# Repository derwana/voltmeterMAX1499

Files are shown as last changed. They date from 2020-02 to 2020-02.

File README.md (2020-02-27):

# voltmeterMAX1499
The voltmeterMAX1499 is - as you may expect by the name - a voltmeter based on the MAX1499 chip by maximinterated.

Started as a university project (v1) to be put into the student laboratories consoles as a highly accurat voltmeter (guess what: it never happend), it later got reworked (v2) to be used with a refrence voltage and two different seven-segment-display-boards.

## 1 precepts
1. boards for the IC and the 'display' have to be seperate
2. board dimensions not given, but as small as possible
3. six seven-segments – one for the '-' and five for the digits
4. multiple options for displaying (0kR for selection)
	1. decimals by chip
	2. decimals by user
5. boards to be connected by male and female headers
6. drills for spacers and mounting
7. use smd parts

## 2 prototype pictures
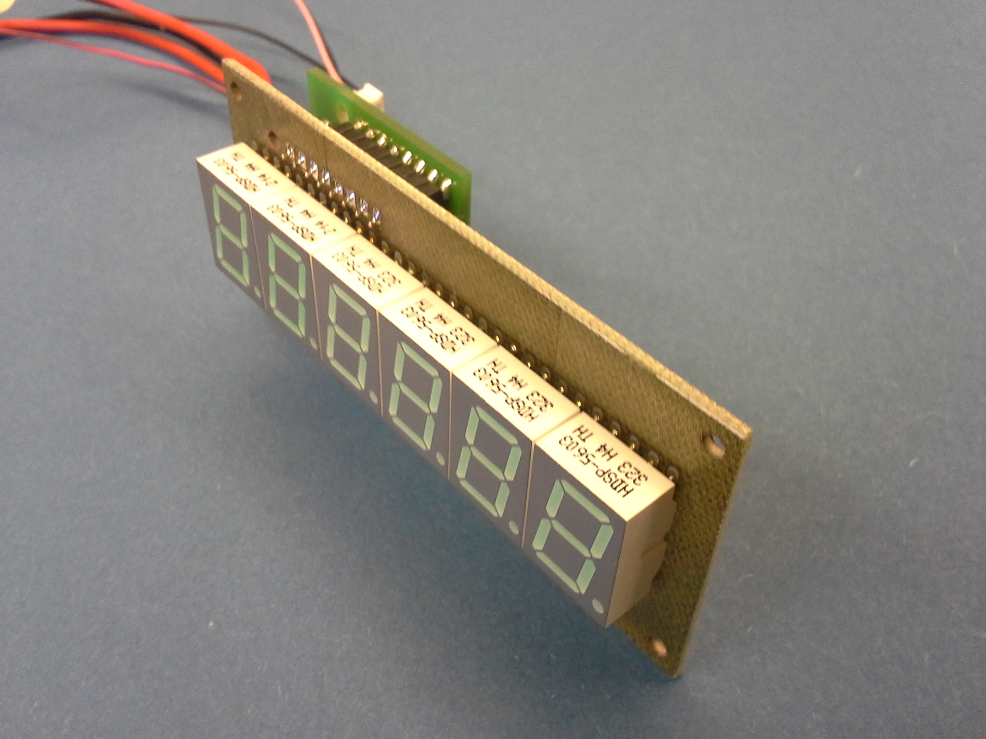
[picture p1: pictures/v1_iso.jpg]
prototype v1

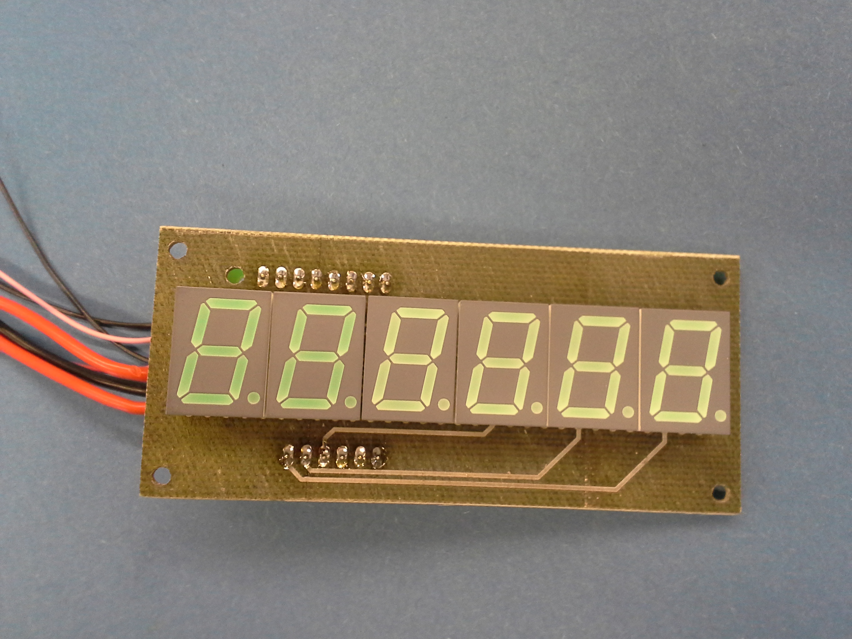
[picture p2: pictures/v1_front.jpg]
prototype v1 front

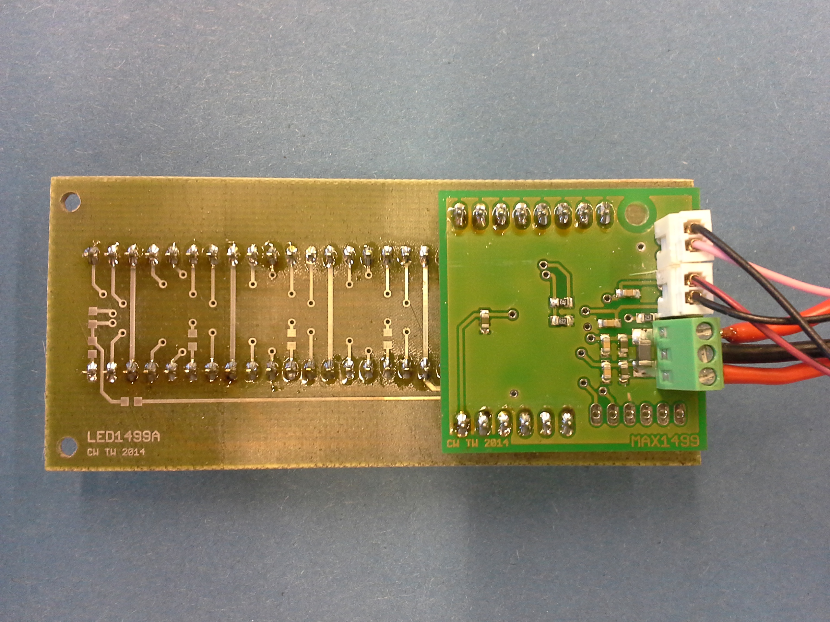
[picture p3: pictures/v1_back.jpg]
prototype v1 back


## 3 prototype testing
on X3: 5V DC (Vcc)
on X1: 1.000V DC (testvoltage by signalgenerator)

Measuring the current consumption is a good tool to determin a correctly working board.

One seven-segment-element consumes 20mA on max brightness and all tiles lit. Six of them are used, so a current consumption of ca. 120mA is expected.

With R3=24kR and displaying 18882, the current flowing is 117mA.
On idle, current consumption as expected of the datasheet.

## 4 Costs
estimated 45,00 € (per unit)
* PCBs 16.65€
* MAX1499 13.10€
* 7-Segments 1.00€-2.00€ (per segment-unit)

## 5 pictures of v2
Connections:
* potentiometer for dimming (black/pink)
* Vcc (black/red)
* voltage to measure (black/orange)
* programming interface (brown/red/orange/yellow)

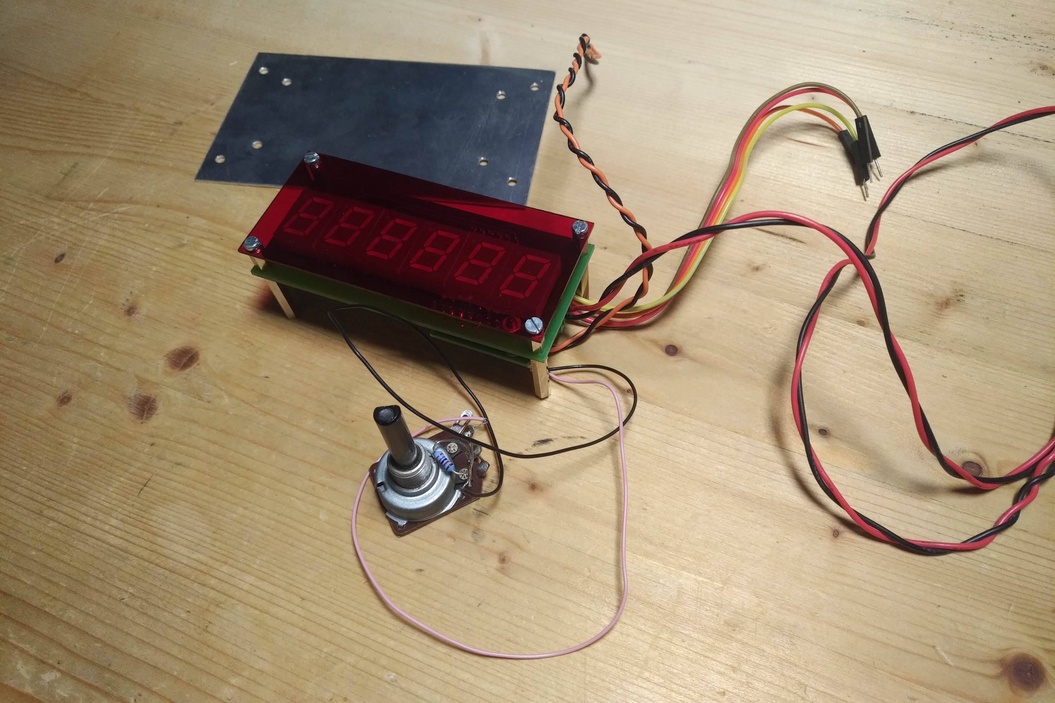
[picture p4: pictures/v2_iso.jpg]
prototype v2

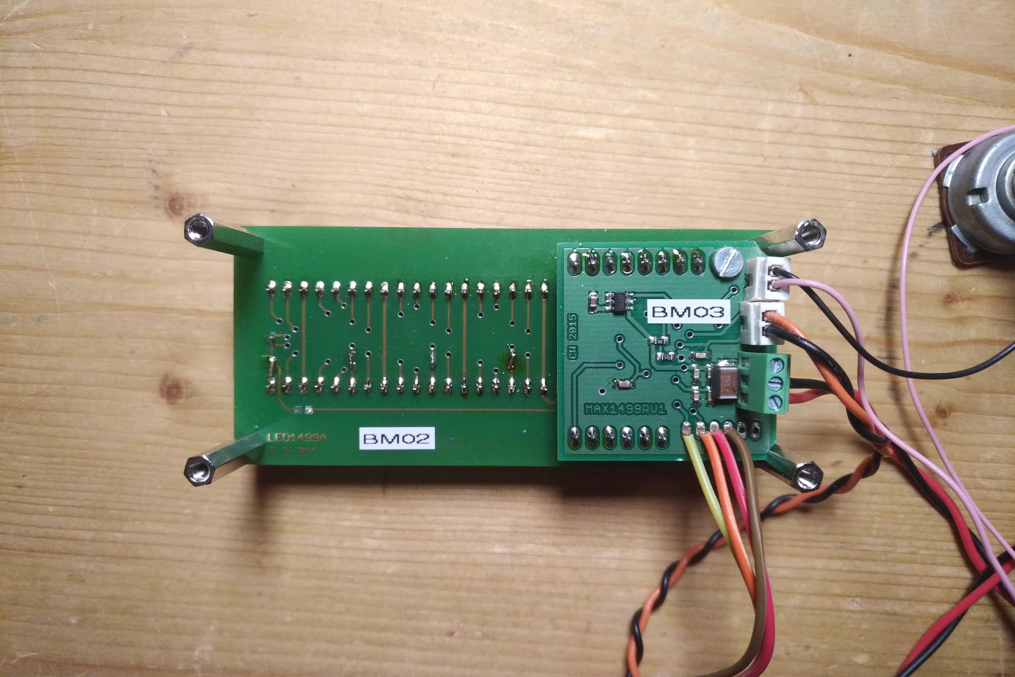
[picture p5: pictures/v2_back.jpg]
prototype v2 back


## 6 further possible improvements (by programming)
* moving decimal point
* using internal reference of MAX1499
* reading measurements over serial

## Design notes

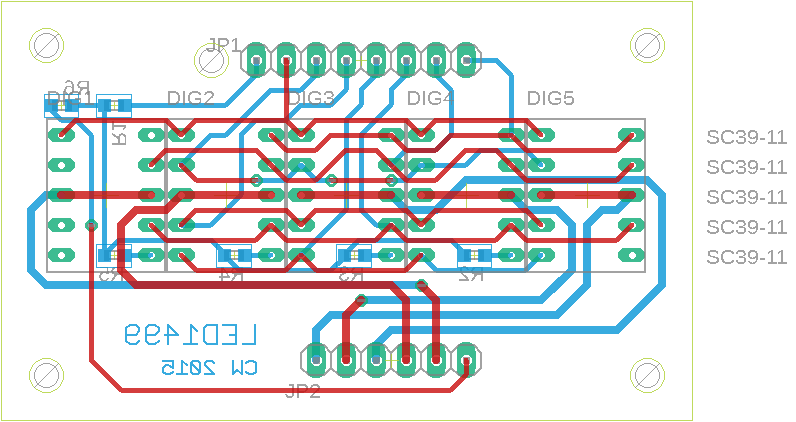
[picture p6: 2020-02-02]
mini_digitboard/mini_digitboard_brd.png

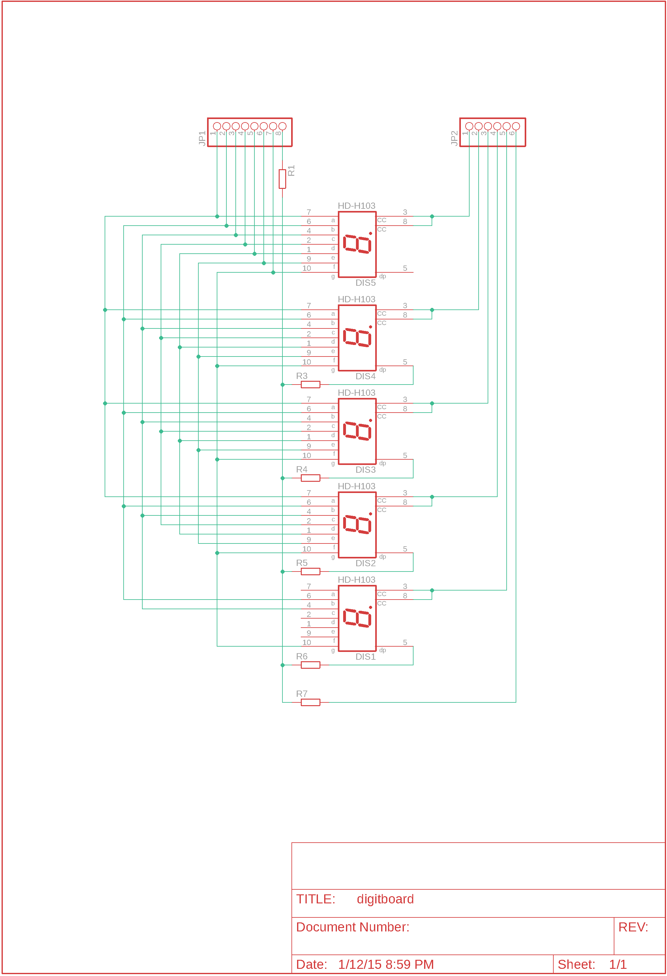
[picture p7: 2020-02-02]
digitboard/digitboard_sch.png

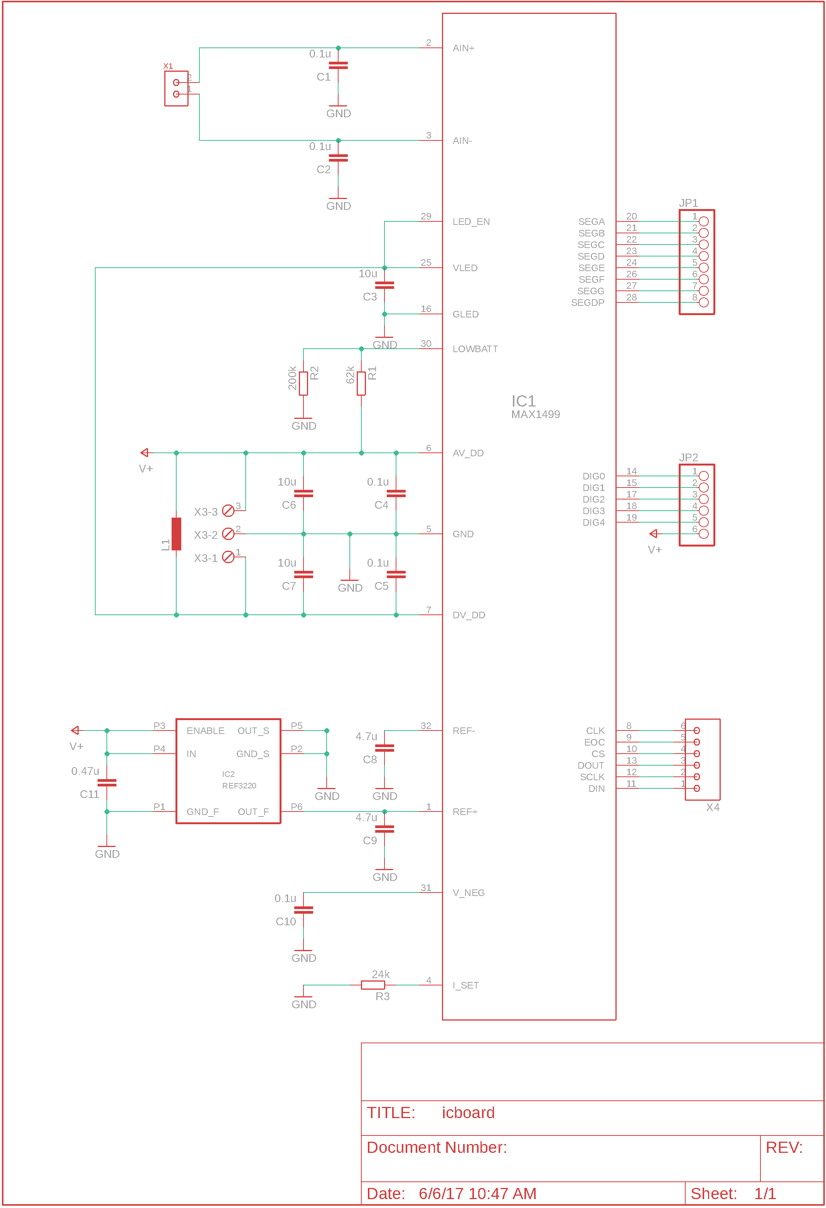
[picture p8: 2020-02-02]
icboard/icboard_sch.png

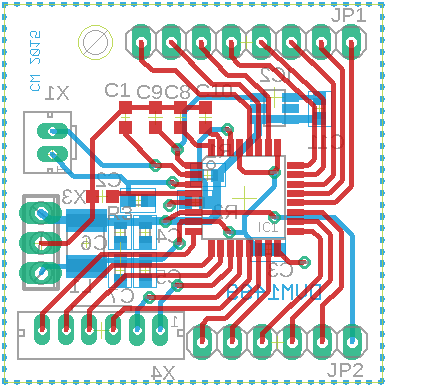
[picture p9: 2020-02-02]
icboard/icboard_brd.png

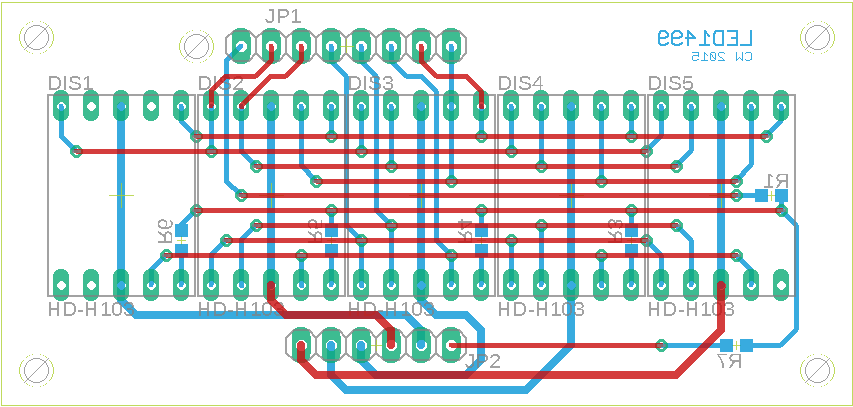
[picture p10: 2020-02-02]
digitboard/digitboard_brd.png

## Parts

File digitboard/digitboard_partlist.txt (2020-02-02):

Partlist

Assembly variant: 

Part     Value          Device     Package  Sheet

DIS1     HD-H103        HD-H103    HDSP-M   1
DIS2     HD-H103        HD-H103    HDSP-M   1
DIS3     HD-H103        HD-H103    HDSP-M   1
DIS4     HD-H103        HD-H103    HDSP-M   1
DIS5     HD-H103        HD-H103    HDSP-M   1
JP1                     PINHD-1X8  1X08     1
JP2                     PINHD-1X6  1X06     1
R1                      R-EU_R0603 R0603    1
R3                      R-EU_R0603 R0603    1
R4                      R-EU_R0603 R0603    1
R5                      R-EU_R0603 R0603    1
R6                      R-EU_R0603 R0603    1
R7                      R-EU_R0603 R0603    1

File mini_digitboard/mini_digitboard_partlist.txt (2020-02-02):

Partlist

Assembly variant: 

Part     Value          Device     Package  Sheet

DIG1     SC39-11        SC39-11    SC39-11  1
DIG2     SC39-11        SC39-11    SC39-11  1
DIG3     SC39-11        SC39-11    SC39-11  1
DIG4     SC39-11        SC39-11    SC39-11  1
DIG5     SC39-11        SC39-11    SC39-11  1
JP1                     PINHD-1X8  1X08     1
JP2                     PINHD-1X6  1X06     1
R1                      R-EU_R0603 R0603    1
R2                      R-EU_R0603 R0603    1
R3                      R-EU_R0603 R0603    1
R4                      R-EU_R0603 R0603    1
R5                      R-EU_R0603 R0603    1
R6                      R-EU_R0603 R0603    1

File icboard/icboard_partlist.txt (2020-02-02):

Partlist

Assembly variant: 

Part     Value          Device        Package   Sheet

C1       0.1u           C-EUC0603     C0603     1
C2       0.1u           C-EUC0603     C0603     1
C3       10u            C-EUC0603     C0603     1
C4       0.1u           C-EUC0603     C0603     1
C5       0.1u           C-EUC0603     C0603     1
C6       10u            C-EUC0603     C0603     1
C7       10u            C-EUC0603     C0603     1
C8       4.7u           C-EUC0603     C0603     1
C9       4.7u           C-EUC0603     C0603     1
C10      0.1u           C-EUC0603     C0603     1
C11      0.47u          C-EUC0603     C0603     1
IC1      MAX1499        MAX1499       TQFP32-08 1
IC2      REF3220        REF3220       REF3220   1
JP1                     PINHD-1X8     1X08      1
JP2                     PINHD-1X6     1X06      1
L1                      L-EUL1812     L1812     1
R1       62k            R-EU_R0603    R0603     1
R2       200k           R-EU_R0603    R0603     1
R3       24k            R-EU_R0603    R0603     1
X1       MOLEX_CON2_2P  MOLEX_CON2_2P CON2_2P   1
X3                      MPT3          3POL254   1
X4                      MOLEX_CON2_6P CON2_6P   1

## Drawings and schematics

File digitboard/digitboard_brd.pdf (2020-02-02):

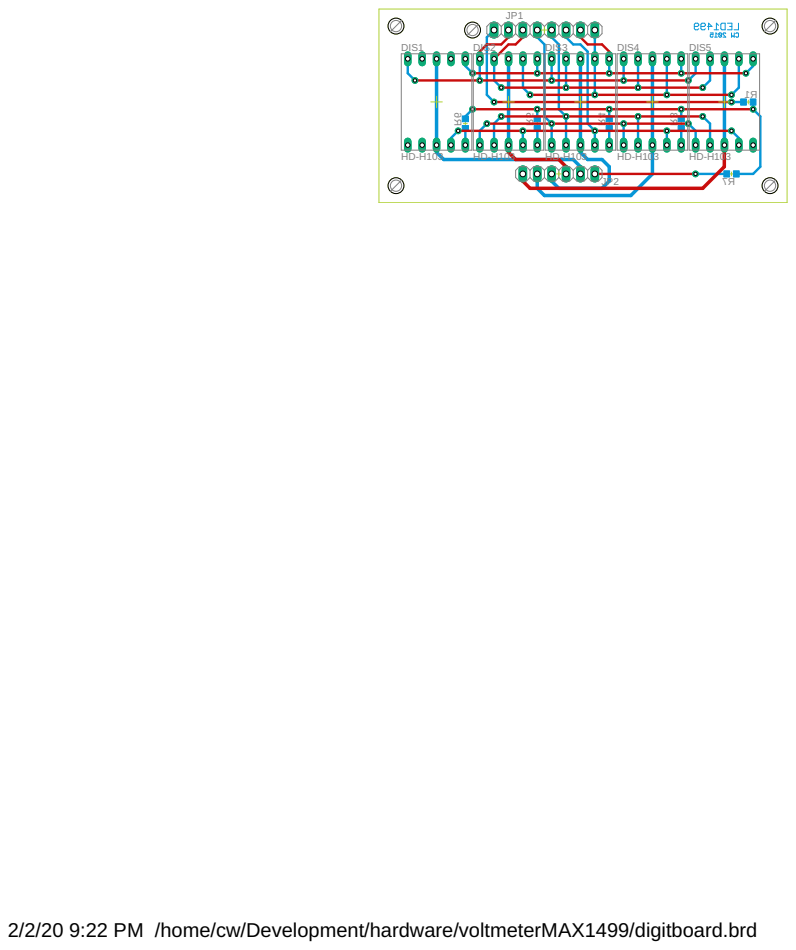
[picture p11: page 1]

2/2/20 9:22 PM /home/cw/Development/hardware/voltmeterMAX1499/digitboard.brd

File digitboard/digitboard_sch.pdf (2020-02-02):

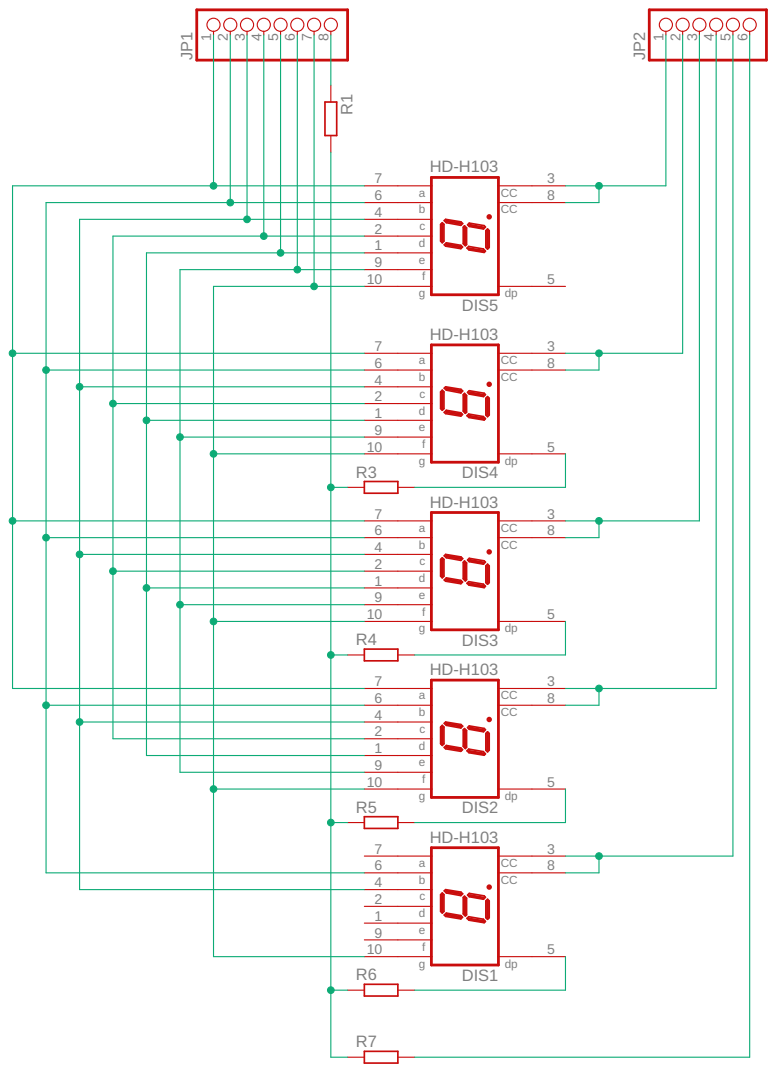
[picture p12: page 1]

a 6 | | CC
4 b | | 8 DIS5 CC 5

2 cd
9 e

a 6 | CC
4 b | 8 DIS4 CC 5

4 b | 8 DIS3 CC 5

6 a | CC
4 b | 8 DIS2 CC 5

4 b | 8 DIS1 CC 5

Document Number: | REV:

Date: 1/12/15 8:59 PM | Sheet: 1/1

2/2/20 9:22 PM /home/cw/Development/hardware/voltmeterMAX1499/digitboard.sch (Sheet: 1/1)

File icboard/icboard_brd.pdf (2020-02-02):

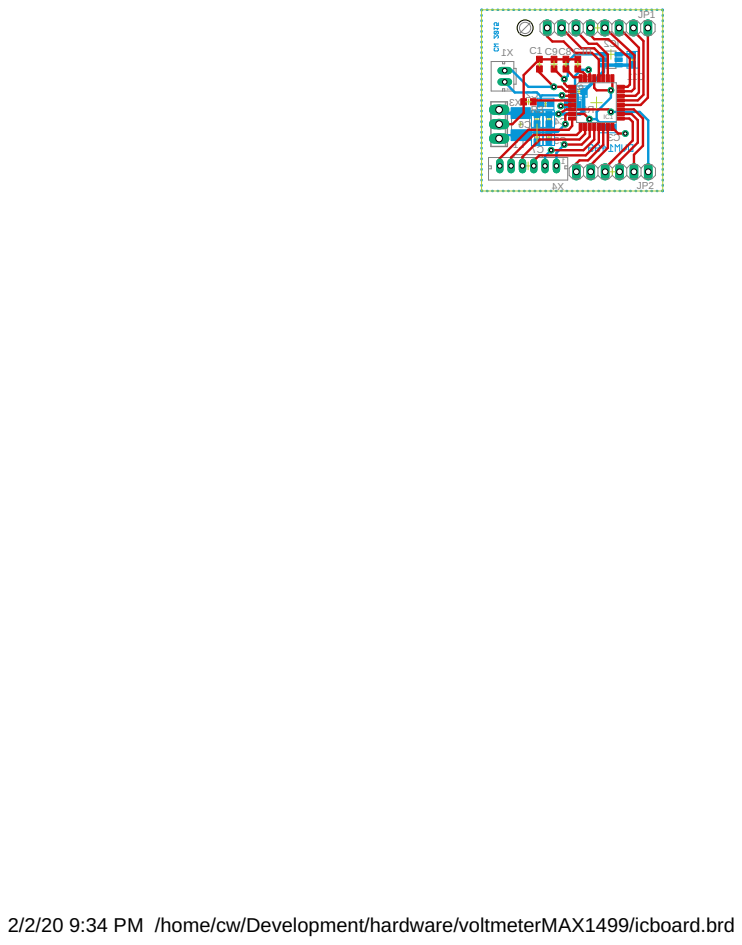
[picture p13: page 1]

2/2/20 9:34 PM /home/cw/Development/hardware/voltmeterMAX1499/icboard.brd

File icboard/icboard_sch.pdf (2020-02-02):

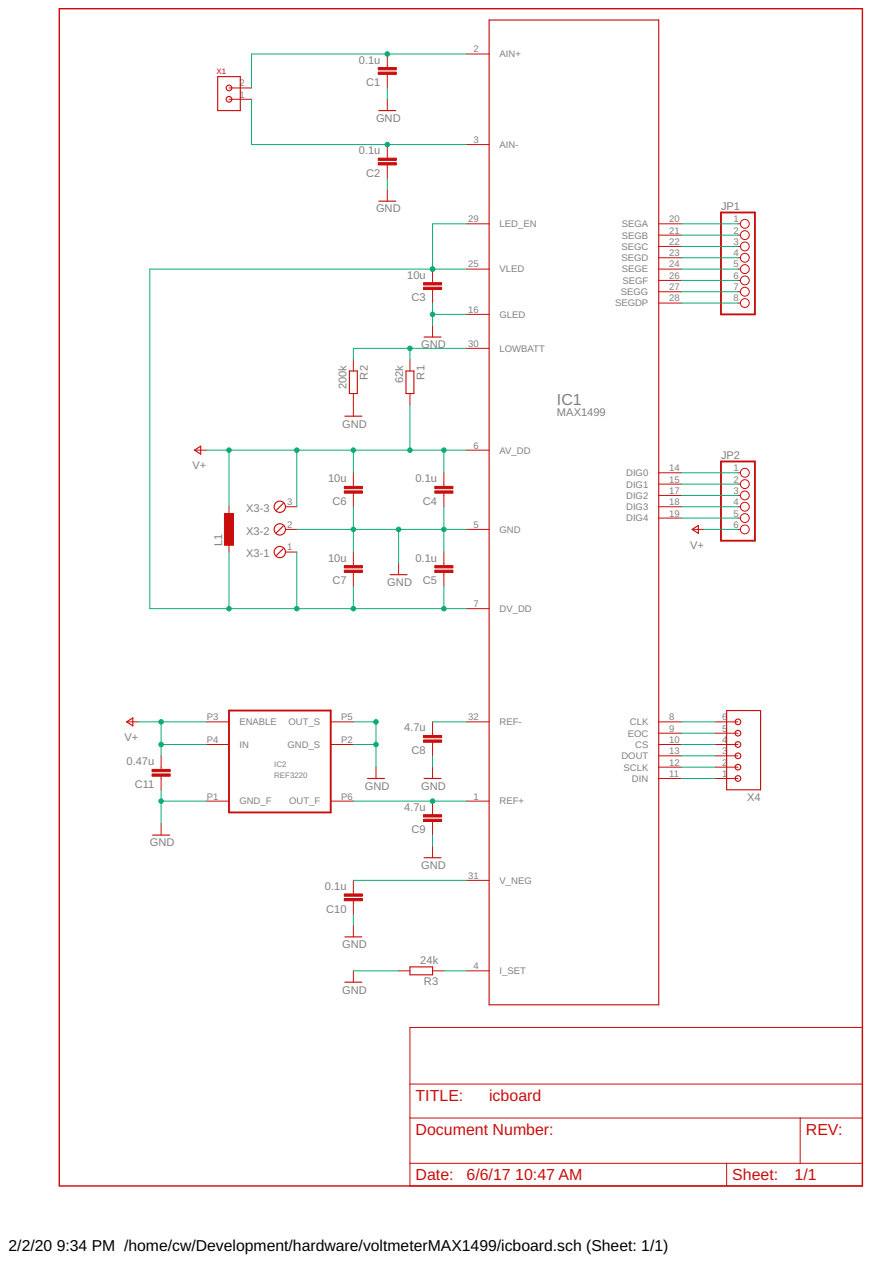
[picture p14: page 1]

Document Number: | REV:

Date: 6/6/17 10:47 AM | Sheet: 1/1

2/2/20 9:34 PM /home/cw/Development/hardware/voltmeterMAX1499/icboard.sch (Sheet: 1/1)

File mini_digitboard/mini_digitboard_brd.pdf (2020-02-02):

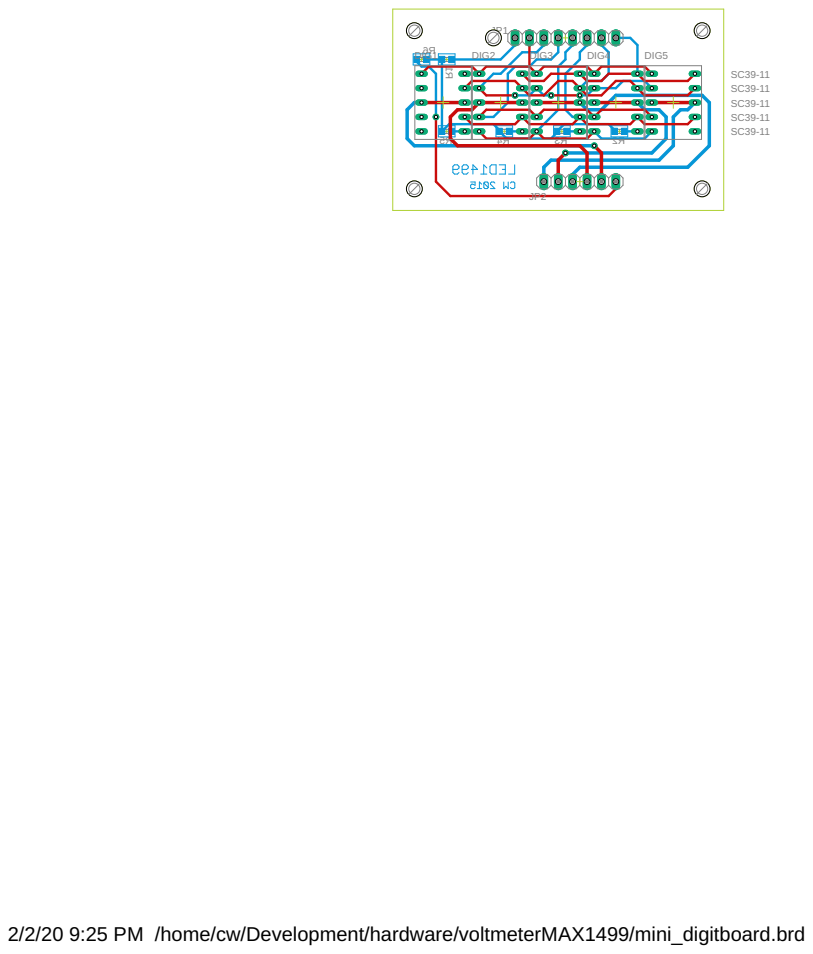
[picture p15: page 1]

2/2/20 9:25 PM /home/cw/Development/hardware/voltmeterMAX1499/mini_digitboard.brd

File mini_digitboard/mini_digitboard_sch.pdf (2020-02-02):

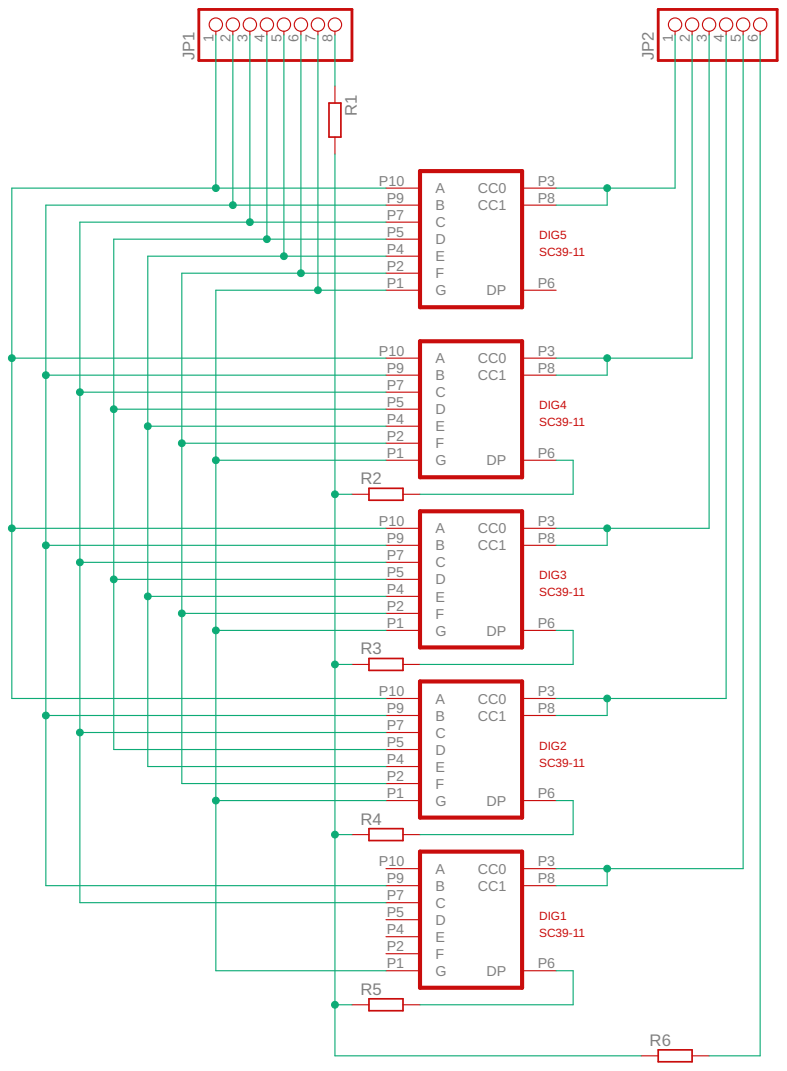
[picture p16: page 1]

Document Number: | REV:

Date: 1/20/15 11:01 AM | Sheet: 1/1

2/2/20 9:25 PM /home/cw/Development/hardware/voltmeterMAX1499/mini_digitboard.sch (Sheet: 1/1)

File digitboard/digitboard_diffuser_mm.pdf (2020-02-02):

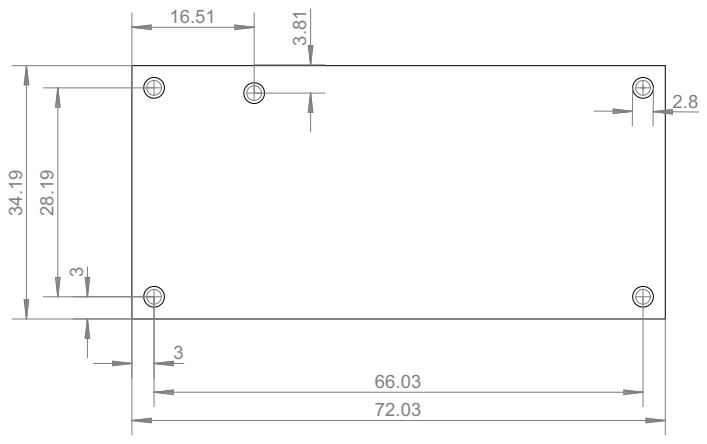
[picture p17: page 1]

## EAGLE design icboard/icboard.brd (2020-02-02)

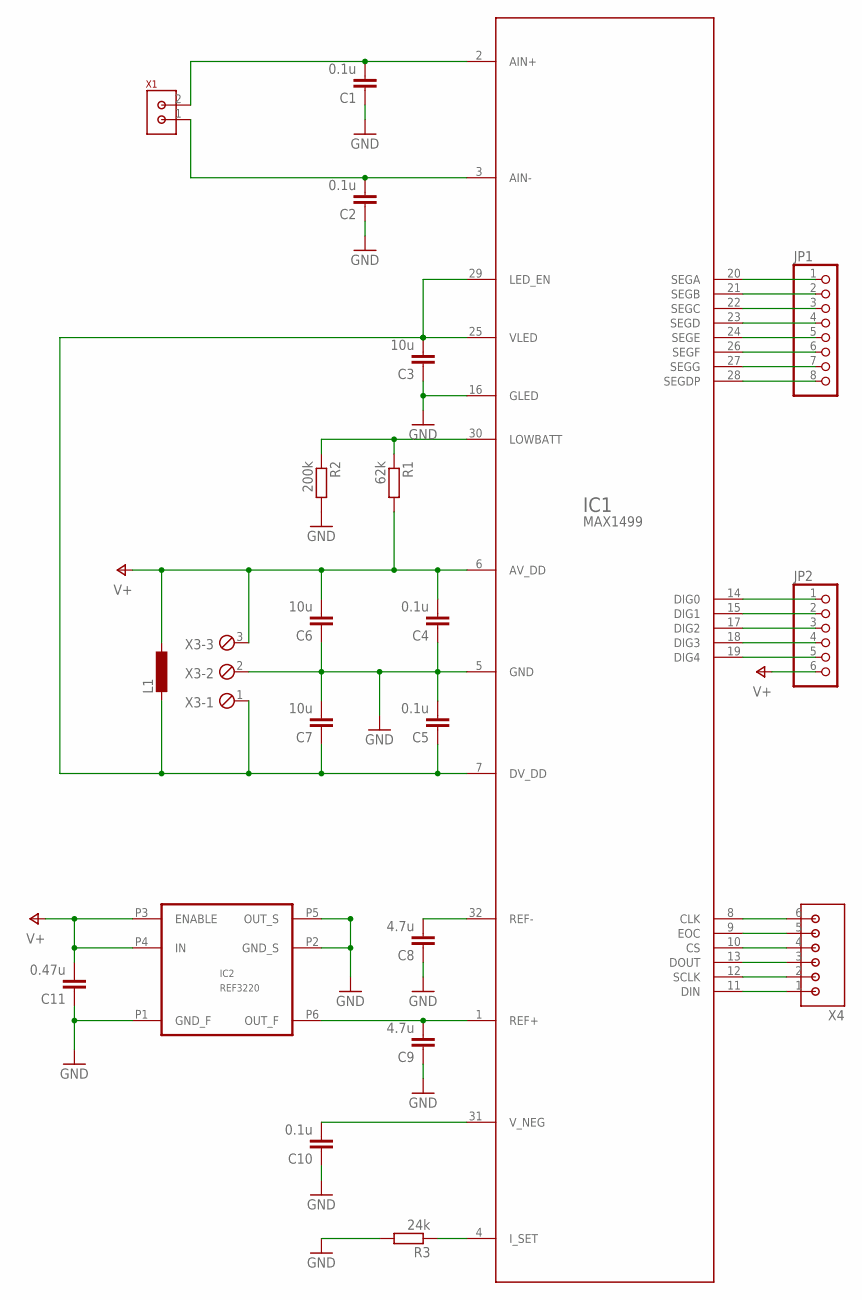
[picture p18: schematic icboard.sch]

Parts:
C1, C2, C4, C5, C10: 0.1u; C0603
C3, C6, C7: 10u; C0603
C8, C9: 4.7u; C0603
C11: 0.47u; C0603
IC1: MAX1499; TQFP32-08
IC2: REF3220
JP1: PINHD-1X8; 1X08
JP2: PINHD-1X6; 1X06
L1: L-EUL1812; L1812
R1: 62k; R0603
R2: 200k; R0603
R3: 24k; R0603
X1: MOLEX_CON2_2P; CON2_2P
X3: MPT3; 3POL254
X4: MOLEX_CON2_6P; CON2_6P

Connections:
AIN+: C1.2, IC1.2 (AIN+), X1.2
AIN-: C2.2, IC1.3 (AIN-), X1.1
CLK: IC1.8 (CLK), X4.6
CS: IC1.10 (CS), X4.4
DIG0: IC1.14 (DIG0), JP2.1
DIG1: IC1.15 (DIG1), JP2.2
DIG2: IC1.17 (DIG2), JP2.3
DIG3: IC1.18 (DIG3), JP2.4
DIG4: IC1.19 (DIG4), JP2.5
DIN: IC1.11 (DIN), X4.1
DOUT: IC1.13 (DOUT), X4.3
DV_DD: C3.2, C5.1, C7.1, IC1.7 (DV_DD), IC1.25 (VLED), IC1.29 (LED_EN), L1.2, X3.1
EOC: IC1.9 (EOC), X4.5
GND: C1.1, C2.1, C3.1, C4.1, C5.2, C6.1, C7.2, C8.1, C9.1, C10.1, C11.1, IC1.5 (GND), IC1.16 (GLED), IC2.P1 (GND_F), IC2.P2 (GND_S), IC2.P5 (OUT_S), R2.2, R3.2, X3.2
I_SET: IC1.4 (I_SET), R3.1
LOWBAT: IC1.30 (LOWBATT), R1.1, R2.1
REF+: C9.2, IC1.1 (REF+), IC2.P6 (OUT_F)
REF-: C8.2, IC1.32 (REF-)
SCLK: IC1.12 (SCLK), X4.2
SEGA: IC1.20 (SEGA), JP1.1
SEGB: IC1.21 (SEGB), JP1.2
SEGC: IC1.22 (SEGC), JP1.3
SEGD: IC1.23 (SEGD), JP1.4
SEGDP: IC1.28 (SEGDP), JP1.8
SEGE: IC1.24 (SEGE), JP1.5
SEGF: IC1.26 (SEGF), JP1.6
SEGG: IC1.27 (SEGG), JP1.7
V+: C4.2, C6.2, C11.2, IC1.6 (AV_DD), IC2.P3 (ENABLE), IC2.P4 (IN), JP2.6, L1.1, R1.2, X3.3
V_NEG: C10.2, IC1.31 (V_NEG)

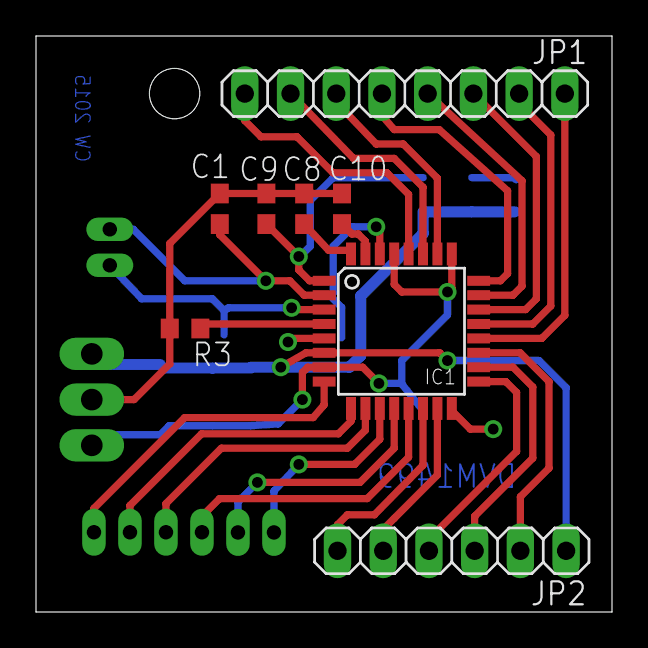
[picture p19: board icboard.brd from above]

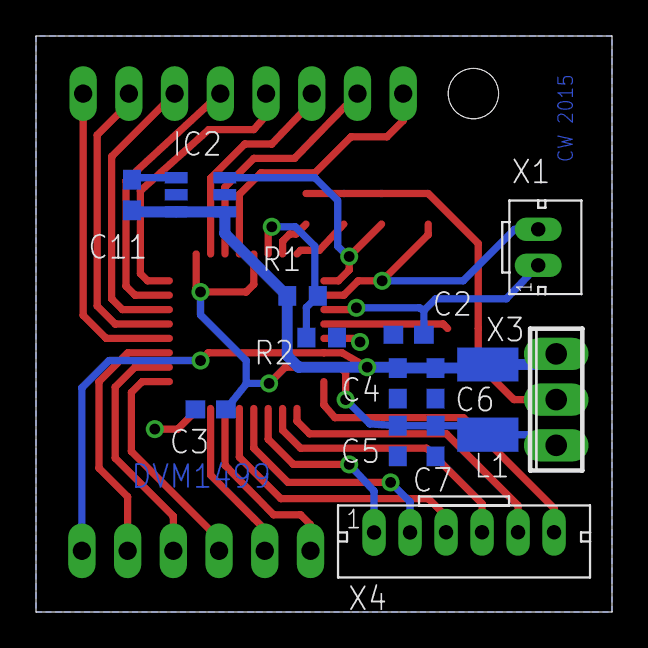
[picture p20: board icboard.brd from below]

Board: 2 copper layers, 32.0 x 32.0 mm, 22 parts (14 on the bottom side), 29 nets.

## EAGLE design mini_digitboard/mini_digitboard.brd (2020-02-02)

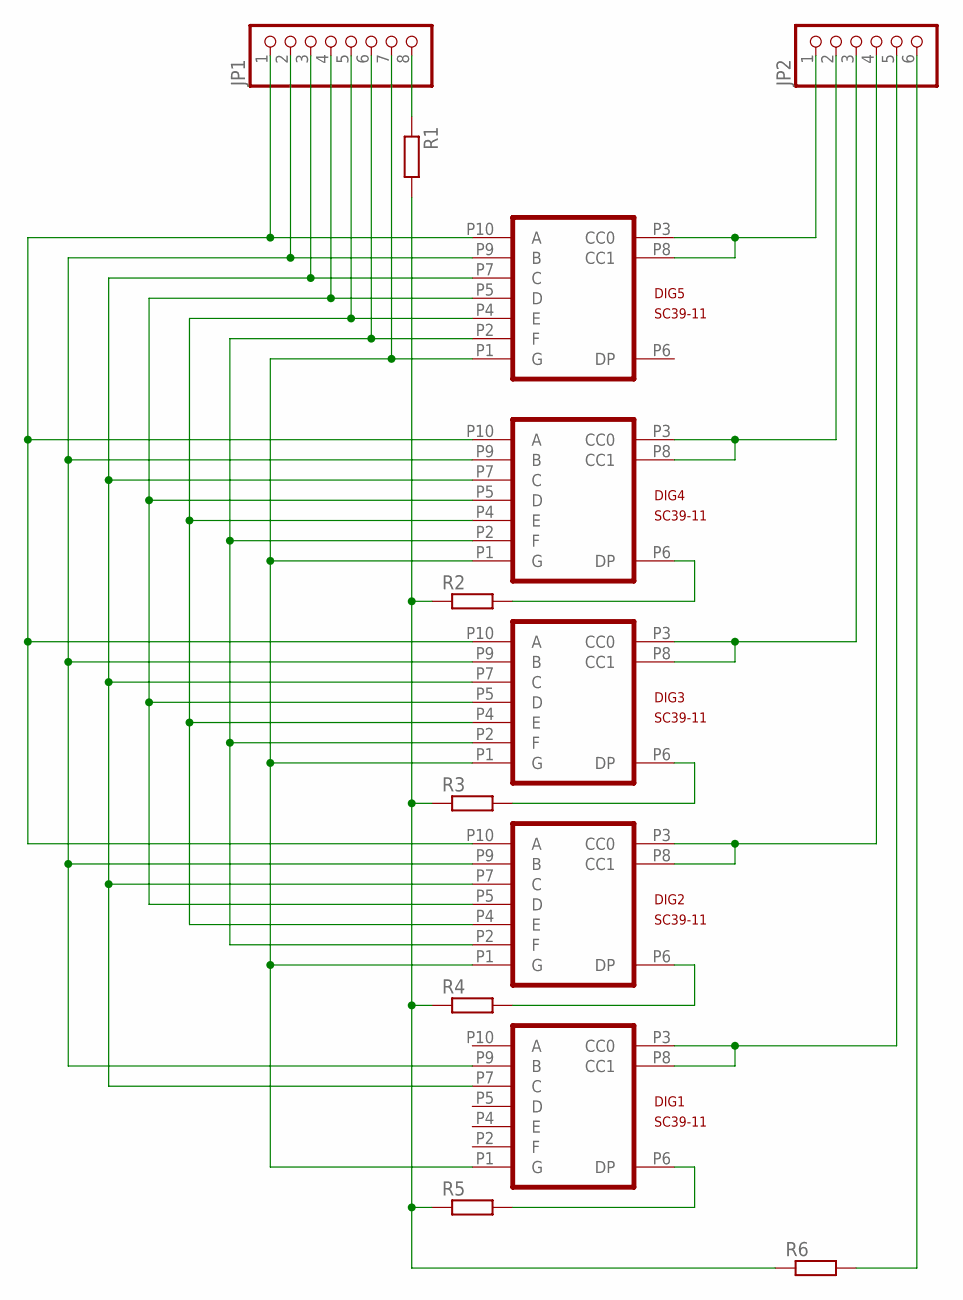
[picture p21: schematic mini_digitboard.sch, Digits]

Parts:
DIG1, DIG2, DIG3, DIG4, DIG5: SC39-11
JP1: PINHD-1X8; 1X08
JP2: PINHD-1X6; 1X06
R1, R2, R3, R4, R5, R6: R-EU_R0603; R0603

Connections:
unnamed: JP2.6, R6.2
unnamed: R1.2, R2.1, R3.1, R4.1, R5.1, R6.1
unnamed: JP1.8, R1.1
unnamed: DIG4.P6 (DP), R2.2
unnamed: DIG3.P6 (DP), R3.2
unnamed: DIG2.P6 (DP), R4.2
unnamed: DIG1.P6 (DP), R5.2
unnamed: DIG1.P1 (G), DIG2.P1 (G), DIG3.P1 (G), DIG4.P1 (G), DIG5.P1 (G), JP1.7
unnamed: DIG2.P10 (A), DIG3.P10 (A), DIG4.P10 (A), DIG5.P10 (A), JP1.1
unnamed: DIG1.P9 (B), DIG2.P9 (B), DIG3.P9 (B), DIG4.P9 (B), DIG5.P9 (B), JP1.2
unnamed: DIG1.P7 (C), DIG2.P7 (C), DIG3.P7 (C), DIG4.P7 (C), DIG5.P7 (C), JP1.3
unnamed: DIG2.P5 (D), DIG3.P5 (D), DIG4.P5 (D), DIG5.P5 (D), JP1.4
unnamed: DIG2.P4 (E), DIG3.P4 (E), DIG4.P4 (E), DIG5.P4 (E), JP1.5
unnamed: DIG2.P2 (F), DIG3.P2 (F), DIG4.P2 (F), DIG5.P2 (F), JP1.6
unnamed: DIG5.P3 (CC0), DIG5.P8 (CC1), JP2.1
unnamed: DIG4.P3 (CC0), DIG4.P8 (CC1), JP2.2
unnamed: DIG3.P3 (CC0), DIG3.P8 (CC1), JP2.3
unnamed: DIG2.P3 (CC0), DIG2.P8 (CC1), JP2.4
unnamed: DIG1.P3 (CC0), DIG1.P8 (CC1), JP2.5

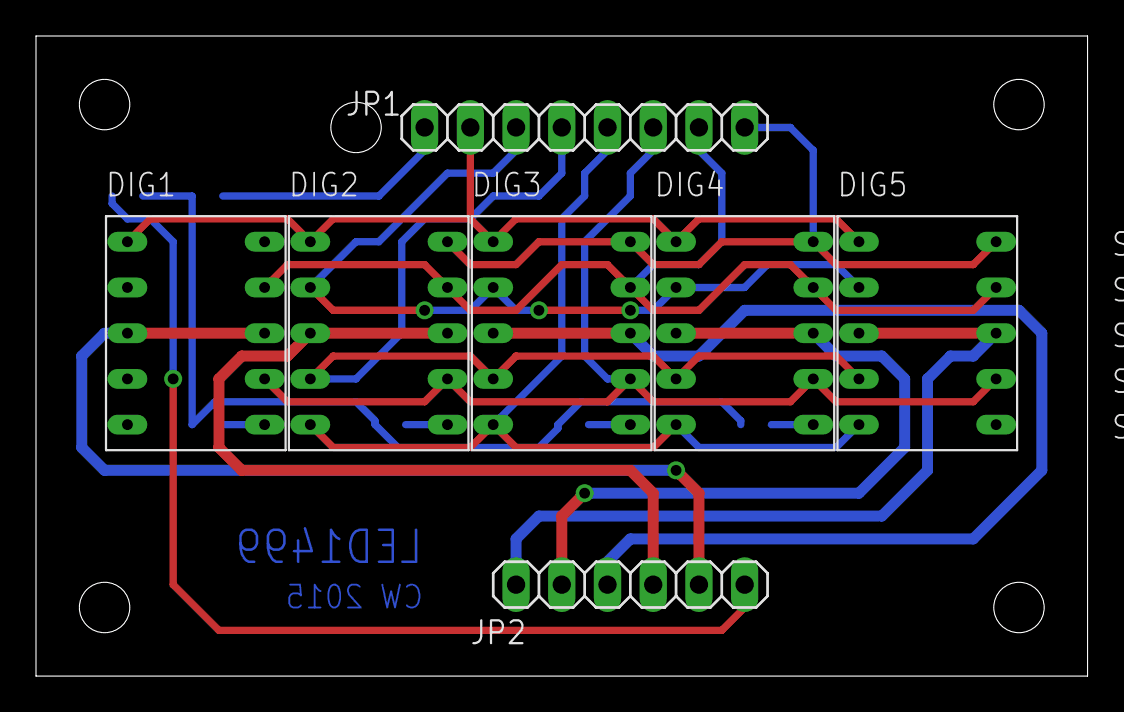
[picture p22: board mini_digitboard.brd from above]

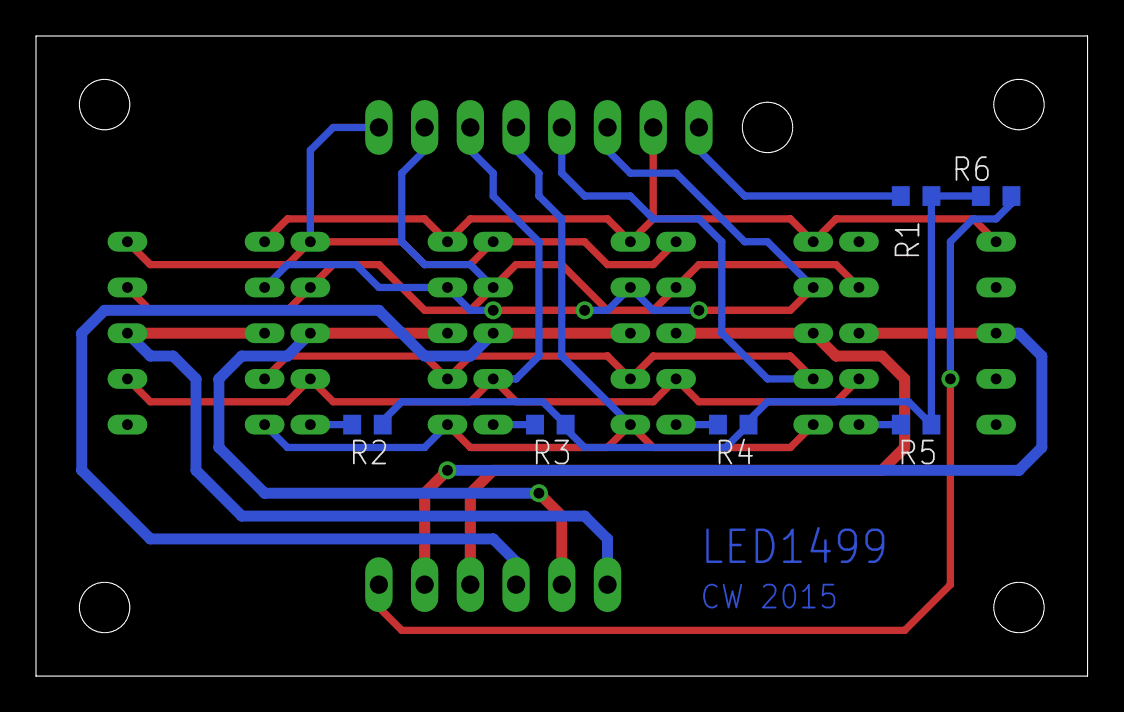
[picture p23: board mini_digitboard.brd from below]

Board: 2 copper layers, 58.4 x 35.6 mm, 13 parts (6 on the bottom side), 19 nets.

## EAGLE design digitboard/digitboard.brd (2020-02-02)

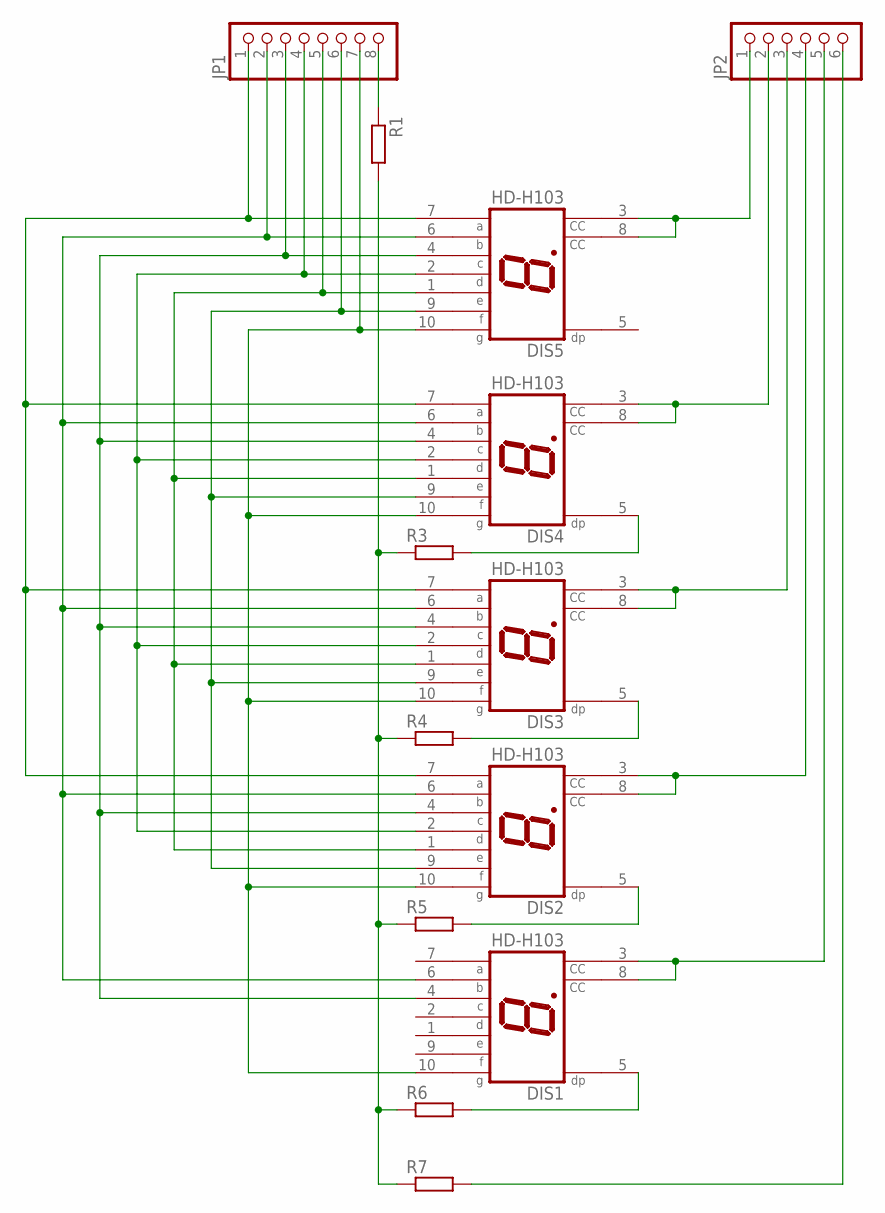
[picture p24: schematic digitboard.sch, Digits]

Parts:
DIS1, DIS2, DIS3, DIS4, DIS5: HD-H103; HDSP-M
JP1: PINHD-1X8; 1X08
JP2: PINHD-1X6; 1X06
R1, R3, R4, R5, R6, R7: R-EU_R0603; R0603

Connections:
unnamed: JP2.6, R7.2
unnamed: R1.2, R3.1, R4.1, R5.1, R6.1, R7.1
unnamed: JP1.8, R1.1
unnamed: DIS4.5 (DP), R3.2
unnamed: DIS3.5 (DP), R4.2
unnamed: DIS2.5 (DP), R5.2
unnamed: DIS1.5 (DP), R6.2
unnamed: DIS2.7 (A), DIS3.7 (A), DIS4.7 (A), DIS5.7 (A), JP1.1
unnamed: DIS1.6 (B), DIS2.6 (B), DIS3.6 (B), DIS4.6 (B), DIS5.6 (B), JP1.2
unnamed: DIS1.4 (C), DIS2.4 (C), DIS3.4 (C), DIS4.4 (C), DIS5.4 (C), JP1.3
unnamed: DIS2.2 (D), DIS3.2 (D), DIS4.2 (D), DIS5.2 (D), JP1.4
unnamed: DIS2.1 (E), DIS3.1 (E), DIS4.1 (E), DIS5.1 (E), JP1.5
unnamed: DIS2.9 (F), DIS3.9 (F), DIS4.9 (F), DIS5.9 (F), JP1.6
unnamed: DIS1.10 (G), DIS2.10 (G), DIS3.10 (G), DIS4.10 (G), DIS5.10 (G), JP1.7
unnamed: DIS5.3 (CC), DIS5.8 (CC), JP2.1
unnamed: DIS4.3 (CC), DIS4.8 (CC), JP2.2
unnamed: DIS3.3 (CC), DIS3.8 (CC), JP2.3
unnamed: DIS2.3 (CC), DIS2.8 (CC), JP2.4
unnamed: DIS1.3 (CC), DIS1.8 (CC), JP2.5

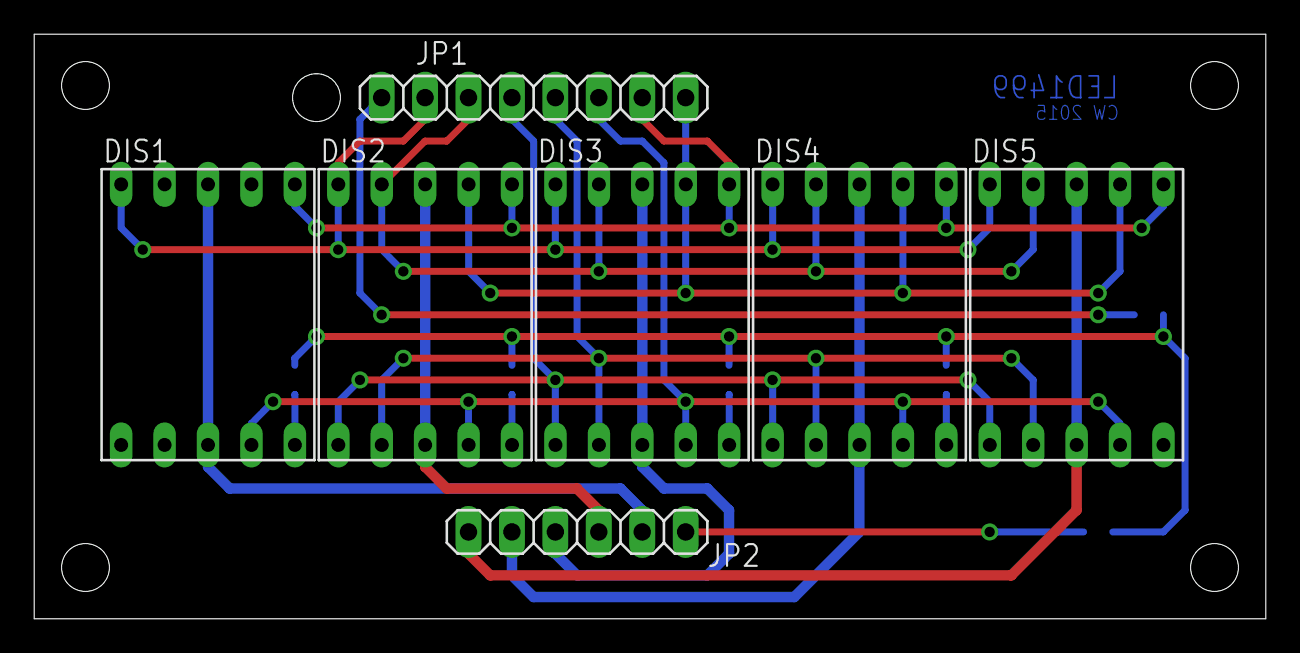
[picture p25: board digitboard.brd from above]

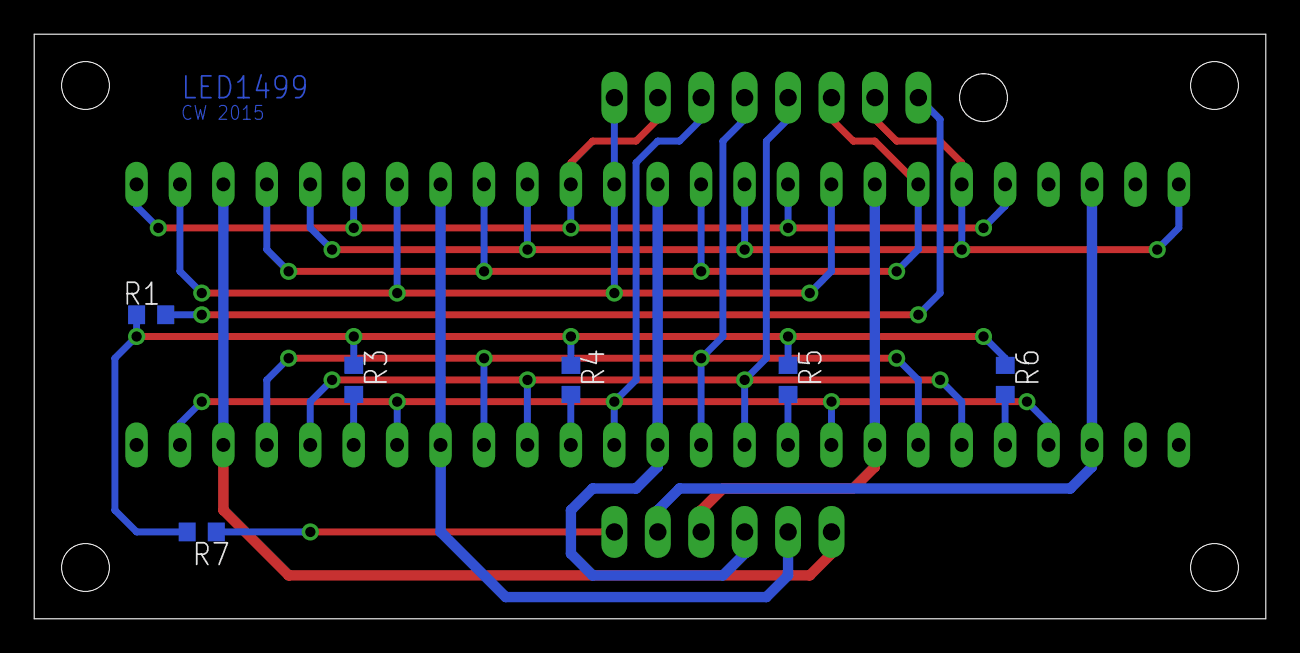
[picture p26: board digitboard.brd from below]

Board: 2 copper layers, 72.0 x 34.2 mm, 13 parts (6 on the bottom side), 19 nets.

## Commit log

2020-02-02 added *.brd and *.sch files
    [digitboard.brd, digitboard.sch, icboard.brd, icboard.sch]
2020-02-02 added pdfs of boards and schematics
2020-02-02 added pngs of boards and schematics
2020-02-02 added digitboard *.brd and *.sch
    [digitboard.brd, digitboard.sch]
2020-02-02 added mini_digitboard *.brd and *.sch
    [mini_digitboard.brd, mini_digitboard.sch]
2020-02-02 added icboard *.brd and *.sch
    [icboard.brd, icboard.sch]
2020-02-02 added folder structure
    [digitboard.brd, digitboard.sch, icboard.brd, icboard.sch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]
2020-02-02 added pictures of prototype
